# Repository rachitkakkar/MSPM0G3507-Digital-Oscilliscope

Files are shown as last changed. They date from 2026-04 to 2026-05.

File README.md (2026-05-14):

# MSPM0G3507 Digital Storage Oscilloscope

This repository contains the firmware for an Digital Storage Oscilloscope, developed for the Texas Instruments **MSPM0G3507** microcontroller. The project leverages interrupt-driven sampling, real-time graphics rendering to an ST7735 TFT LCD display, and interactive peripherals on a custom PCB designed in KiCAD.

Demo 1
*Low quality GIF displaying oscilloscope at different frequencies*

Demo 1
*Low quality GIF displaying scope at different zoom levels (controlled via slide pot)*

## Features

- **High-Speed Signal Acquisition**: There is a 50 kHz hardware timer interrupt (TimerG6) to sample the ADC and store the value in a storage buffer. The process of sampling and storing into the buffer only occurs on the rising edge of the signal after it passes a trigger set at the half-way mark in order to capture stable waveforms.
- **Real-Time Display**: Live waveform plotting on an ST7735 TFT LCD with grid generation and zoom. Displaying the waveform only occurs when the buffer is full, upon which the 50 kHz TimerG6 interrupt is disabled in order to plot values onto the LCD. Without this crucial step, the microcontroller would be interrupted before it had time to write to the display as that is a comparatively slow task relative to the frequent timer interrupts. In order to further speed up the display (and prevent the flickering of a whole screen redraw), a buffer of previous samples is stored and only the pixels of the previous waveform are cleared. This also requires dynamically fixing the grid in those spots.
- **Interactive Measurements**: 
  - Dual horizontal and vertical cursors to measure $\Delta V$, $\Delta T$.
  - Real-time on-screen calculations for Peak-to-Peak Voltage ($V_{pp}$) and Frequency.
- **Dynamic Controls**:
  - Discrete zoom levels (1x, 2x, 4x) controlled by an ADC-sampled slide potentiometer and downsampling of the ADC sample buffer.
  - Hardware switch integration for playback control (Play/Pause), cursor selection, and precise cursor movement.
  - Input control is handled by another periodic hardware timer interrupt (TimerG12), this time at a frequency of only 30 Hz.
- **Audio Feedback**: DAC-driven sound generation mapped to UI interactions for tactile and auditory feedback. The audio files are downsampled and stored into a C array, where a periodic SysTick interrupt then outputs the values to the 5-bit DAC on the PCB at a frequency of 11 kHz. To prevent noticeable audio distortion, this interrupt is the highest priority.
- **Localization**: Built-in dual-language support (English and Spanish) for the on-screen display.
- **Debugging**: LED based triple toggle to determine latency of interrupt handler.

## Architecture and Key Components

- **`Lab9HMain.cpp`**: The primary entry point. Registers the 30 Hz UI/Game engine timer interrupt, the 50 kHz ADC sampling timer interrupt, the 11 kHz SysTick interrupt, and the main application loop. Also stores code for the corresponding IRQ handlers.
- **`Oscilloscope.cpp` / `.h`**: Core oscilloscope logic. Handles ADC configuration, sample buffering, trigger-level synchronization, and signal metrics calculations (Frequency, $V_{pp}$).
- **`ST7735.cpp` / `.h`**: Display driver for the SPI-based LCD, including routines for drawing bitmaps, characters, and primitive shapes.
- **`Cursor` & `Application`**: Encapsulates the UI state, grid drawing, and cursor boundary/overlap logic.
- **Peripherals**: Interfaces for `Clock`, `Timer`, `Switch`, `SlidePot`, `LED`, `Sound`, and `DAC5`.

## Hardware

- **Microcontroller**: TI MSPM0G3507 LaunchPad
- **Display**: ST7735 SPI LCD (Adafruit REDTAB or HiLetGo BLACKTAB)
- **Inputs**: 
  - Slide Potentiometer (ADC input)
  - 4 Tactile Switches (Digital GPIO)
- **Outputs**: 
  - 5-bit weighted DAC, amplifier chip, and speaker (for audio)
  - LEDs (triple toggle and pause indicator)

The full PCB files are available in the `PCB/` folder
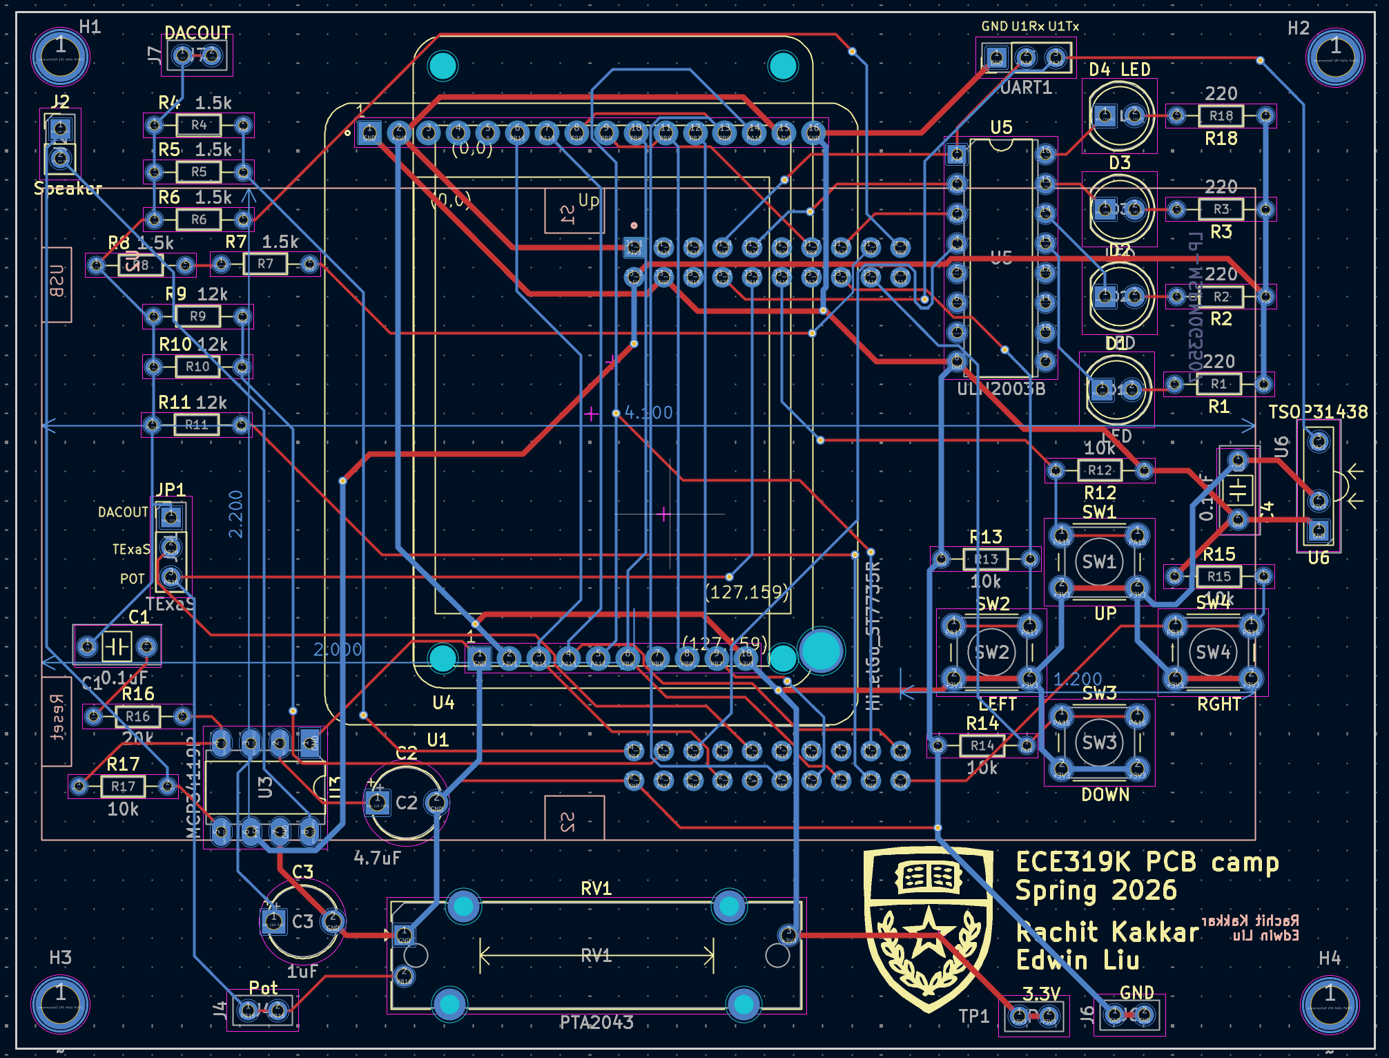
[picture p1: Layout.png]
Layout

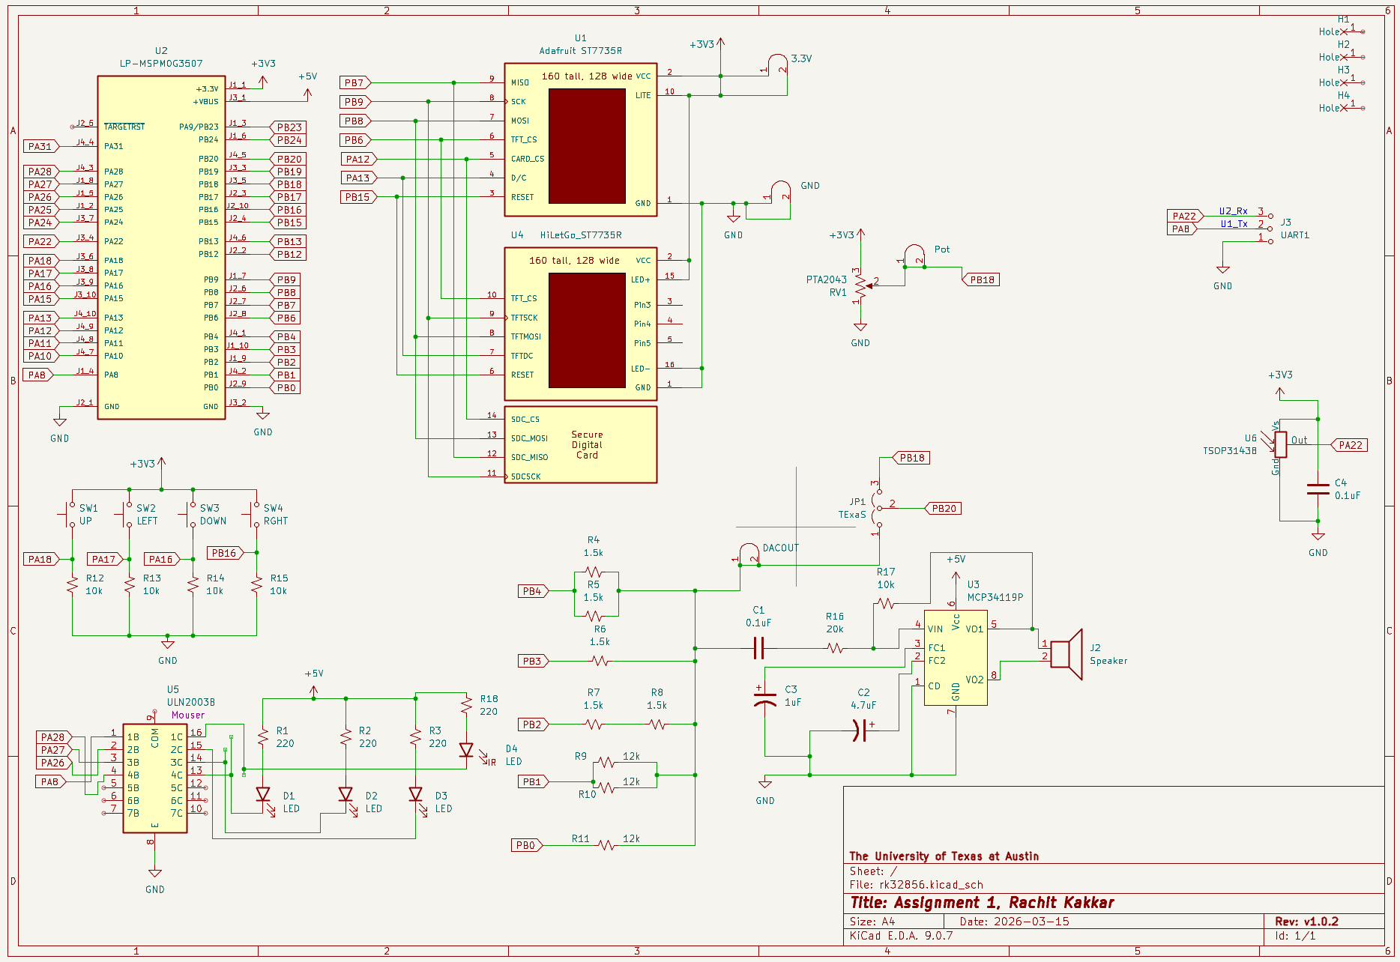
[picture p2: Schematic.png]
Schematic


## Build Instructions

This project is built using Code Composer Studio (CCS) and the TI MSPM0-SDK. 

1. Import the project folder into a Code Composer Studio workspace.
2. Ensure the `MSPM0-SDK` (v2.9.0.01 or compatible) and SysConfig are correctly linked in your project properties.
3. Build the project using the **TI Arm Clang Compiler** (`TICLANG`).
4. Flash the `.out` executable onto the MSPM0G3507 LaunchPad.

## Credits

Much of the starter code for this project was developed by the instructors for ECE319H Course at the University of Texas at Austin.

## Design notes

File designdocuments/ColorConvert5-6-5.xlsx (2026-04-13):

red | green | blue | 565
0 | 255 | 120 | 0x7FE0 | 0x7FE0, // 0, 255, 120

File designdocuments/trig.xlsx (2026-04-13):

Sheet: 64
 | 2 |  | 64
angle | vx | vy | ix | iy
0 | 2 | 0 | 128 | 0
0.09817477042 | 1.990369453 | 0.1960342807 | 127 | 13
0.1963495408 | 1.961570561 | 0.390180644 | 126 | 25
0.2945243113 | 1.913880671 | 0.5805693545 | 122 | 37
0.3926990817 | 1.847759065 | 0.7653668647 | 118 | 49
0.4908738521 | 1.763842529 | 0.9427934737 | 113 | 60
0.5890486225 | 1.662939225 | 1.111140466 | 106 | 71
0.687223393 | 1.546020907 | 1.268786568 | 99 | 81
0.7853981634 | 1.414213562 | 1.414213562 | 91 | 91
0.8835729338 | 1.268786568 | 1.546020907 | 81 | 99
0.9817477042 | 1.111140466 | 1.662939225 | 71 | 106
1.079922475 | 0.9427934737 | 1.763842529 | 60 | 113
1.178097245 | 0.7653668647 | 1.847759065 | 49 | 118
1.276272016 | 0.5805693545 | 1.913880671 | 37 | 122
1.374446786 | 0.390180644 | 1.961570561 | 25 | 126
1.472621556 | 0.1960342807 | 1.990369453 | 13 | 127
1.570796327 | -7.656635742e-16 | 2 | 0 | 128
1.668971097 | -0.1960342807 | 1.990369453 | -13 | 127
1.767145868 | -0.390180644 | 1.961570561 | -25 | 126
1.865320638 | -0.5805693545 | 1.913880671 | -37 | 122
1.963495408 | -0.7653668647 | 1.847759065 | -49 | 118
2.061670179 | -0.9427934737 | 1.763842529 | -60 | 113
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

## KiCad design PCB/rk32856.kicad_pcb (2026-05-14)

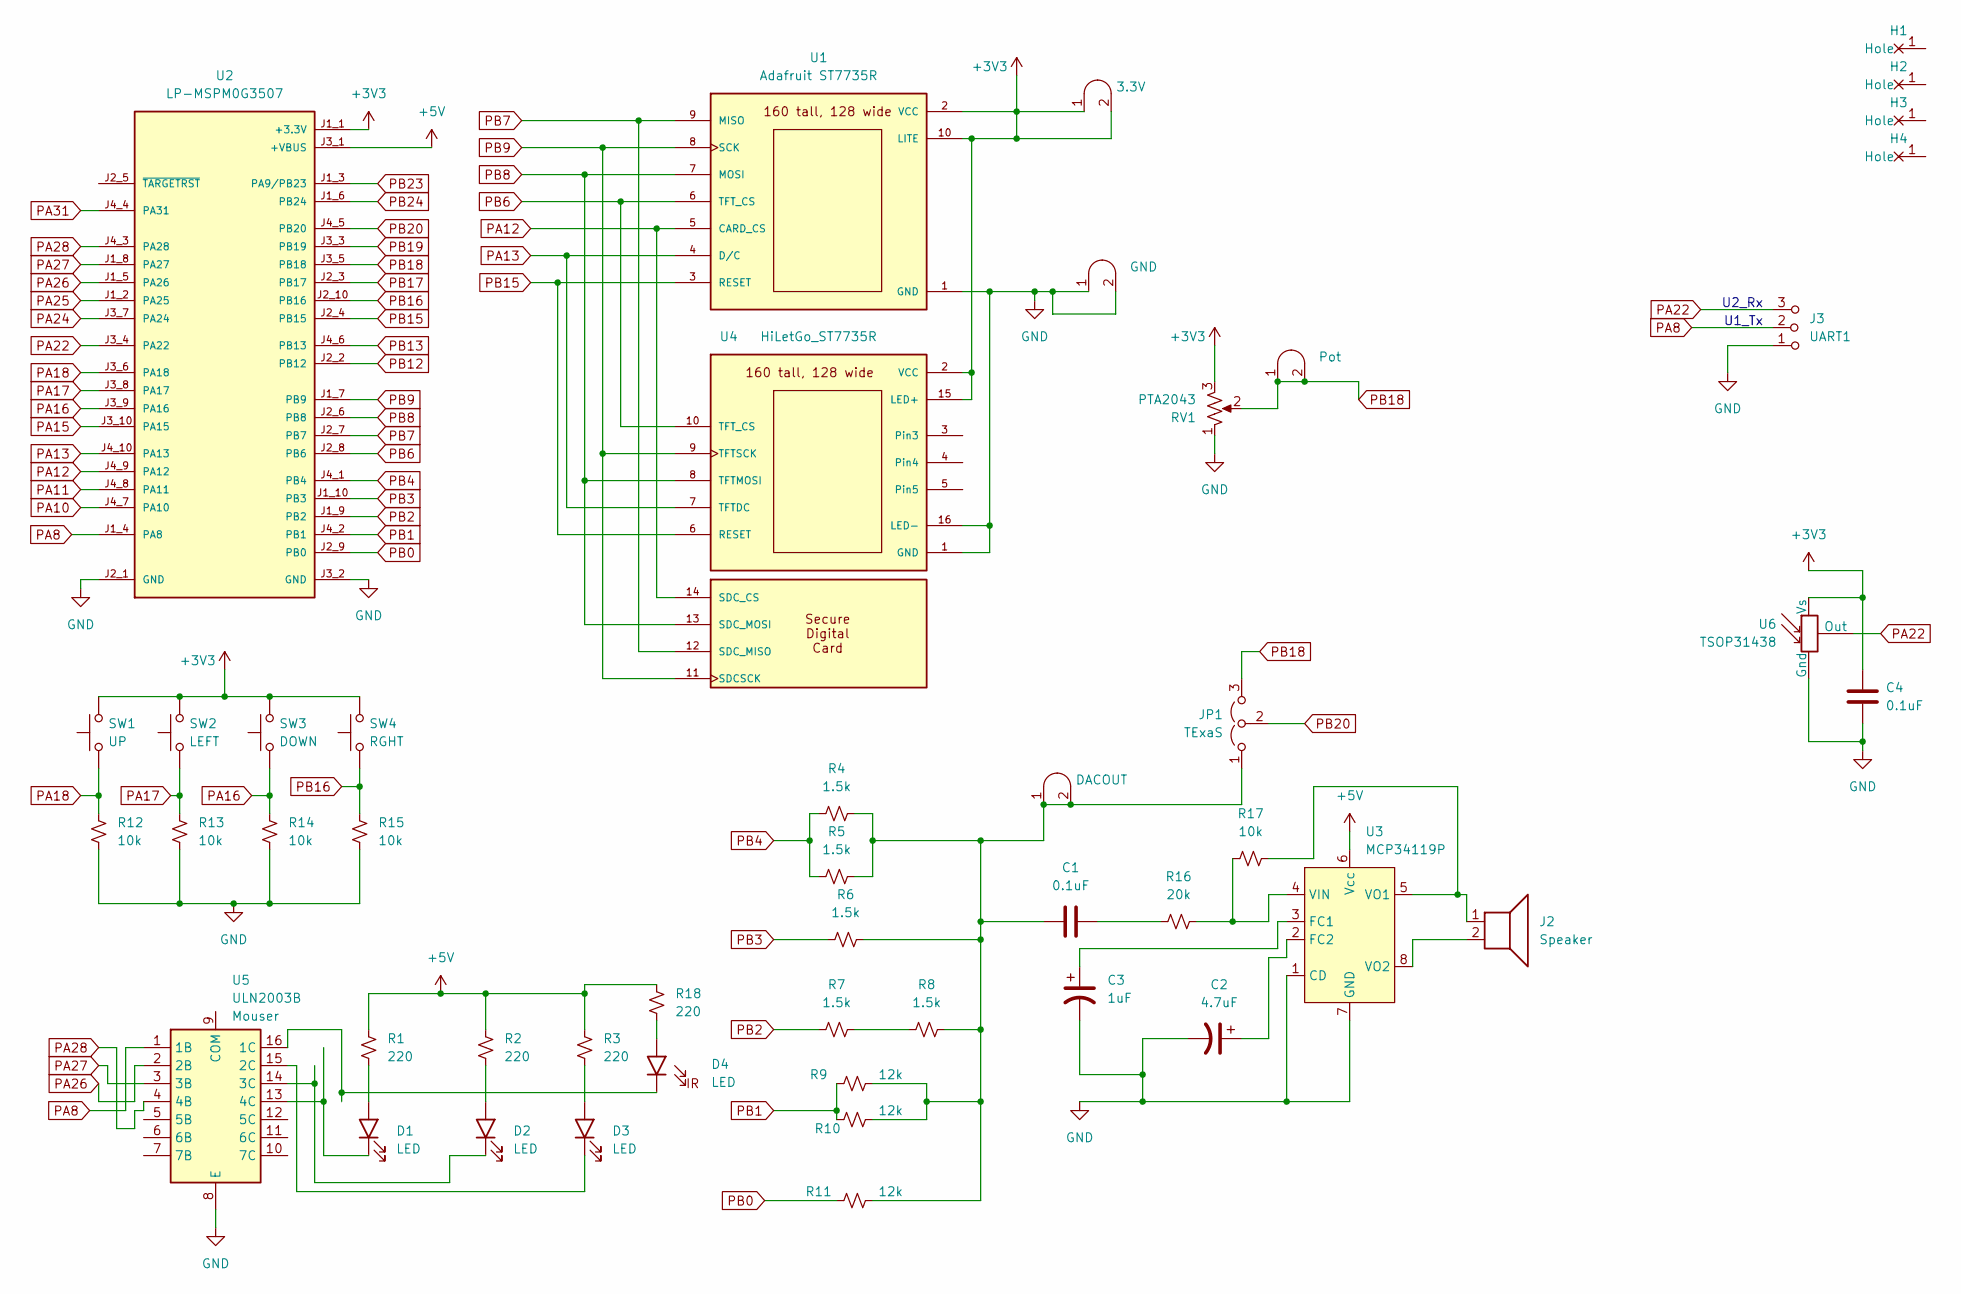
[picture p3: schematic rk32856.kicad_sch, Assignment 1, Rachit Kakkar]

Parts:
C1, C4: 0.1uF; C_Axial_200mil
C2: 4.7uF; CP_Radial_Tantal200mil
C3: 1uF; CP_Radial_Tantal200mil
D1, D2, D3, D4: LED; LED_D5.0mm
H1, H2, H3, H4: MountingHole_4_40
J2: Speaker; PinHeader_1x02_P2.54mm_Vertical
J3: UART1; PinHeader_1x03_P2.54mm_Vertical
J4: Pot; Testpoint_1x02_P2.54mm
J6: GND; Testpoint_1x02_P2.54mm
J7: DACOUT; Testpoint_1x02_P2.54mm
JP1: TExaS; PinHeader_1x03_P2.54mm_Vertical
R1, R2, R3, R18: 220; R_Axial_DIN0204_L3.6mm_D1.6mm_P7.62mm_Horizontal
R4, R5, R6, R7, R8: 1.5k; R_Axial_DIN0204_L3.6mm_D1.6mm_P7.62mm_Horizontal
R9, R10, R11: 12k; R_Axial_DIN0204_L3.6mm_D1.6mm_P7.62mm_Horizontal
R12, R13, R14, R15, R17: 10k; R_Axial_DIN0204_L3.6mm_D1.6mm_P7.62mm_Horizontal
R16: 20k; R_Axial_DIN0204_L3.6mm_D1.6mm_P7.62mm_Horizontal
RV1: PTA2043; PTA2043pot
SW1: UP; SW_PUSH_6mm
SW2: LEFT; SW_PUSH_6mm
SW3: DOWN; SW_PUSH_6mm
SW4: RGHT; SW_PUSH_6mm
TP1: 3.3V; Testpoint_1x02_P2.54mm
U1: Adafruit ST7735R; adafruit_st7735r
U2: LP-MSPM0G3507; ti_LP_MSPM0G3507
U3: MCP34119P; DIP-8_W7.62mm_LongPads
U4: HiLetGo_ST7735R; hiletgo_st7735r
U5: ULN2003B; DIP-16_W7.62mm
U6: TSOP31438

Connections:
+3V3: C4.1, RV1.3, SW1.2, SW2.2, SW3.2, SW4.2, TP1.1 (A), TP1.2 (B), U1.2 (VCC), U1.10 (LITE), U2.J1_1 (+3.3V), U4.2 (VCC), U4.15 (LED+), U6.2 (Vs)
+5V: R1.1, R2.1, R3.1, R18.1, U2.J3_1 (+VBUS), U3.6 (Vcc)
GND: C2.2, C3.2, C4.2, J3.1 (A), J6.1 (A), J6.2 (B), R12.2, R13.2, R14.2, R15.2, RV1.1, U1.1 (GND), U2.J2_1 (GND), U2.J3_2 (GND), U3.1 (CD), U3.7 (GND), U4.1 (GND), U4.16 (LED-), U5.8 (E), U6.1 (Gnd)
unnamed: C1.2, R16.1
unnamed: D1.2 (A), R1.2
unnamed: D1.1 (K), U5.13 (4C)
unnamed: D2.2 (A), R2.2
unnamed: D2.1 (K), U5.14 (3C)
unnamed: D3.2 (A), R3.2
unnamed: D3.1 (K), U5.15 (2C)
unnamed 10: D4.2 (A), R18.2; also elsewhere on the board
unnamed 11: D4.1 (K), U5.16 (1C); also elsewhere on the board
unnamed: C1.1, J7.1 (A), J7.2 (B), JP1.1 (A), R4.1, R5.1, R6.1, R8.1, R9.1, R10.1, R11.1
unnamed: R7.1, R8.2
unnamed: C3.1, U3.3 (FC1)
unnamed: C2.1, U3.2 (FC2)
unnamed: R16.2, R17.1, U3.4 (VIN)
unnamed: J2.1, R17.2, U3.5 (VO1)
unnamed: J2.2, U3.8 (VO2)
PA8: J3.2 (B), U2.J1_4 (PA8), U5.1 (1B)
PA10: U2.J4_7 (PA10)
PA11: U2.J4_8 (PA11)
PA12: U1.5 (CARD_CS), U2.J4_9 (PA12), U4.14 (SDC_CS)
PA13: U1.4 (D/C), U2.J4_10 (PA13), U4.7 (TFTDC)
PA15: U2.J3_10 (PA15)
PA16: R14.1, SW3.1, U2.J3_9 (PA16)
PA17: R13.1, SW2.1, U2.J3_8 (PA17)
PA18: R12.1, SW1.1, U2.J3_6 (PA18)
PA22: J3.3 (C), U2.J3_4 (PA22), U6.3 (Out)
PA24: U2.J3_7 (PA24)
PA25: U2.J1_2 (PA25)
PA26: U2.J1_5 (PA26), U5.2 (2B)
PA27: U2.J1_8 (PA27), U5.3 (3B)
PA28: U2.J4_3 (PA28), U5.4 (4B)
PA31: U2.J4_4 (PA31)
PB0: R11.2, U2.J2_9 (PB0)
PB1: R9.2, R10.2, U2.J4_2 (PB1)
PB2: R7.2, U2.J1_9 (PB2)
PB3: R6.2, U2.J1_10 (PB3)
PB4: R4.2, R5.2, U2.J4_1 (PB4)
PB6: U1.6 (TFT_CS), U2.J2_8 (PB6), U4.10 (TFT_CS)
PB7: U1.9 (MISO), U2.J2_7 (PB7), U4.12 (SDC_MISO)
PB8: U1.7 (MOSI), U2.J2_6 (PB8), U4.8 (TFTMOSI), U4.13 (SDC_MOSI)
PB9: U1.8 (SCK), U2.J1_7 (PB9), U4.9 (TFTSCK), U4.11 (SDCSCK)
PB12: U2.J2_2 (PB12)
PB13: U2.J4_6 (PB13)
PB15: U1.3 (RESET), U2.J2_4 (PB15), U4.6 (RESET)
PB16: R15.1, SW4.1, U2.J2_10 (PB16)
PB17: U2.J2_3 (PB17)
PB18: J4.1 (A), J4.2 (B), JP1.3 (B), RV1.2, U2.J3_5 (PB18)
PB19: U2.J3_3 (PB19)
PB20: JP1.2 (C), U2.J4_5 (PB20)
PB23: U2.J1_3 (PA9/PB23)
PB24: U2.J1_6 (PB24)

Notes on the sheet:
U2_Rx
U1_Tx

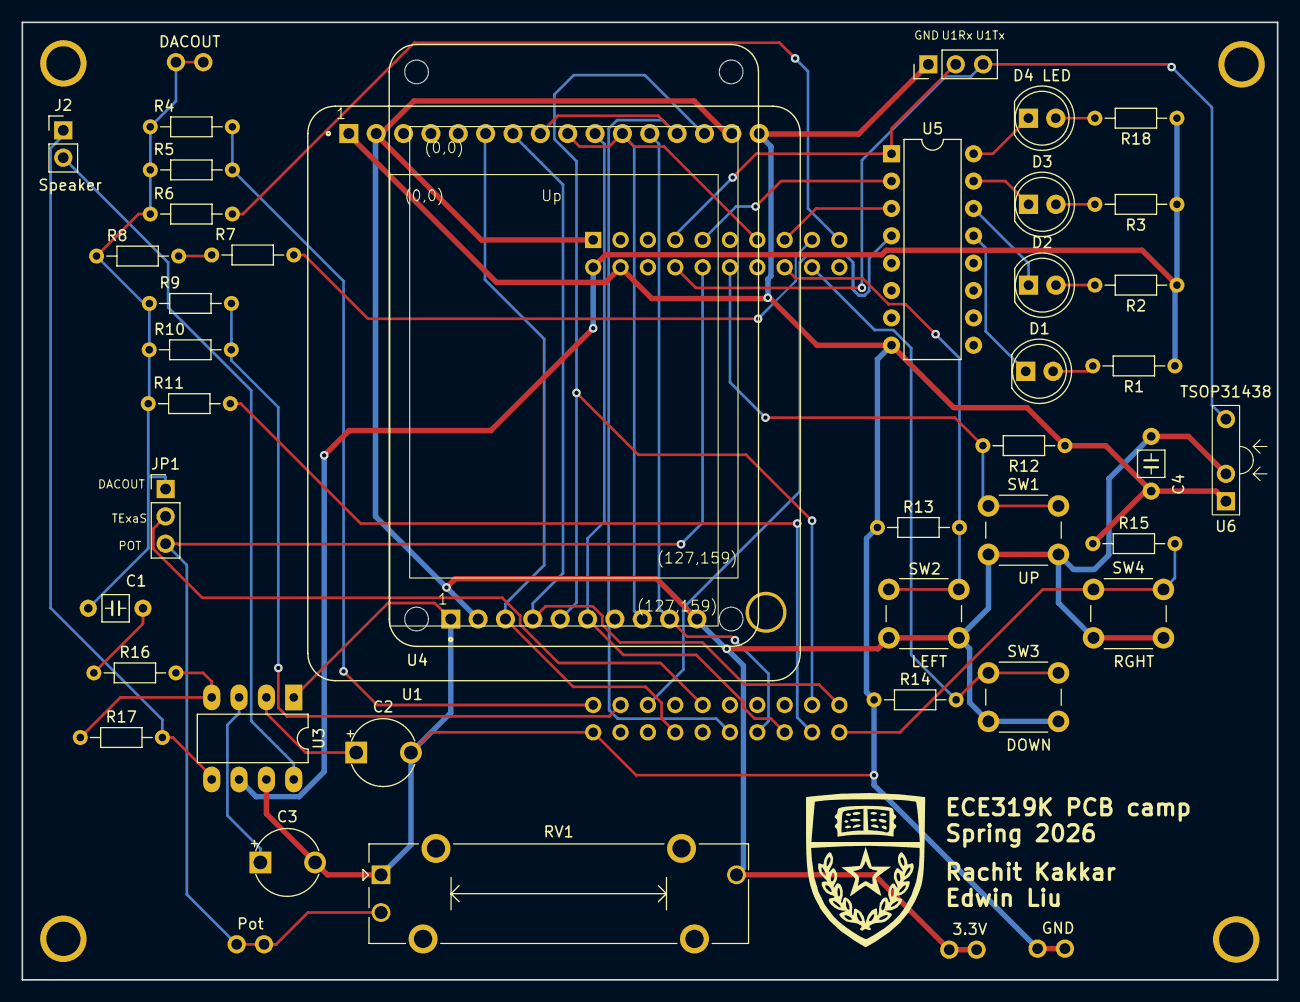
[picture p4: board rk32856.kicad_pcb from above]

Board: 2 copper layers, 116.5 x 88.9 mm, 48 parts (1 on the bottom side), 42 nets.

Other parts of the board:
D4 LED: LED; LED_D5.0mm

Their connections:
unnamed 10: D4 LED.2 (A); also elsewhere on the board
unnamed 11: D4 LED.1 (K); also elsewhere on the board

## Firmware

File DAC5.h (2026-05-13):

/**
 * @file      DAC5.h
 * @brief     5-bit binary-weighted DAC
 * @details   Lab 5. Digital Piano using a Digital to Analog Converter<br>
 * For more information see<br> https://docs.google.com/document/d/1DVmHjqsx24FvLp4x8KKyr5UmDeDlBlfeQPsVvKFQF_k/edit<br>
 * @version   ECE319K Fall 2025
 * @author    Your names go here
 * @copyright Lab solution, do not post,
 * @warning   AS-IS
 * @note      For more information see  http://users.ece.utexas.edu/~valvano/
 * @date      July 19, 2025
  <table>
<caption id="Lab5pins">Pins on the 5-bit DAC</caption>
<tr><th>Pin <th>GPIO<th>Hardware
<tr><td>PB4 <td>output<td>bit 4 (most significant)
<tr><td>PB3 <td>output<td>bit 3
<tr><td>PB2 <td>output<td>bit 2
<tr><td>PB1 <td>output<td>bit 1
<tr><td>PB0 <td>output<td>bit 0 (least significant)
</table>
  ******************************************************************************/
#ifndef __DAC5_H__
#define __DAC5_H__

/**
 * Initialize 5-bit DAC
 *    - PB4 output MSBit
 *    - PB3 output
 *    - PB2 output
 *    - PB1 output
 *    - PB0 output LSBit
 * @param none
 * @return none
 * @brief  Initialize DAC
 * @note LaunchPad_Init has been called; this program should not reset Port B
 */
void DAC5_Init(void);

/**
 * Output to 5-bit DAC
 * @param data is 5-bit value to output, 0 to 31
 * @return none
 * @brief  Output to DAC5
 * @note this solution must be friendly
 */
void DAC5_Out(uint32_t data);

#endif // __DAC5_H__

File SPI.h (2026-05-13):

/*!
 * @defgroup SPI
 * @brief Synchronous serial communication
 <table>
<caption id="SPIpins">SPI-LCD pins </caption>
<tr><th>Pin <th>Function  <th>Description
<tr><td>PB9 <td>SPI1 SCLK <td>J1.7 LCD SPI clock (SPI)   
<tr><td>PB6 <td>SPI1 CS0  <td>J2.13 LCD SPI CS (SPI)     
<tr><td>PB8 <td>SPI1 PICO <td>J2.15 LCD SPI data (SPI)    
<tr><td>PB15<td>GPIO      <td>J2.17 LCD !RST =1 for run, =0 for reset   
<tr><td>PA13<td>GPIO      <td>J4.31 LCD RS =1 for data, =0 for command   
</table>
 * @{*/
/**
 * @file      SPI.h
 * @brief     Synchronous serial communication
 * @details   SPI uses a chip select, clock, data out and data in. This interface does not use data in.
 * This interface can be used for MKII LCD and the ST7735R LCD
 * \image html SPIinterface.png  width=500px
 * @version   ECE319K v1.2
 * @author    Daniel Valvano and Jonathan Valvano
 * @copyright Copyright 2025 by Jonathan W. Valvano, valvano@mail.utexas.edu,
 * @warning   AS-IS
 * @note      For more information see  http://users.ece.utexas.edu/~valvano/
 * @date      July 19, 2025
 <table>
<caption id="SPIpins2">SPI-LCD pins </caption>
<tr><th>Pin <th>Function  <th>Description
<tr><td>PB9 <td>SPI1 SCLK <td>J1.7 LCD SPI clock (SPI)   
<tr><td>PB6 <td>SPI1 CS0  <td>J2.13 LCD SPI CS (SPI)     
<tr><td>PB8 <td>SPI1 PICO <td>J2.15 LCD SPI data (SPI)    
<tr><td>PB15<td>GPIO      <td>J2.17 LCD !RST =1 for run, =0 for reset  
<tr><td>PA13<td>GPIO      <td>J4.31 LCD RS =1 for data, =0 for command   
</table>
  ******************************************************************************/
#ifndef __SPI_H__
#define __SPI_H__


/**
 * Initialize SPI for 8 MHz baud clock
 * using busy-wait synchronization.
 * Calls Clock_Freq to get bus clock
 * - PB9 SPI1 SCLK   
 * - PB6 SPI1 CS0       
 * - PB8 SPI1 PICO  
 * - PB15 GPIO !RST =1 for run, =0 for reset    
 * - PA13 GPIO RS =1 for data, =0 for command
 *
 * @note SPI0,SPI1 in power domain PD1 SysClk equals bus CPU clock
 * @param none
 * @return none 
 * @brief initialize SPI
 */
void SPI_Init(void);

/**
 * Output 8-bit data to SPI port.
 * RS=PA13=1 for data.
 * @param data is an 8-bit data to be transferred
 * @return none 
 * @brief Output data
 */
void SPI_OutData(char data);

/**
 * Output 8-bit command to SPI port.
 * RS=PA13=0 for command
 * @param  command is an 8-bit command to be transferred
 * @return none 
 * @brief Output command
 */
void SPI_OutCommand(char command);

/**
 *  Reset LCD 
 * -# drive RST high for 500ms
 * -# drive RST low for 500ms
 * -# drive RST high for 500ms
 * 
 * @param none
 * @return none 
 * @brief Reset LCD
 */
void SPI_Reset(void);
#endif // __SPI_H__
/** @}*/

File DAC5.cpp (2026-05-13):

/* DAC5.cpp
 * Students put your names here
 * Modified: December 26, 2024
 * 5-bit binary-weighted DAC connected to PB4-PB0
 */
#include <ti/devices/msp/msp.h>
#define PB0INDEX  11 // UART0_TX  SPI1_CS2  TIMA1_C0  TIMA0_C2
#define PB1INDEX  12 // UART0_RX  SPI1_CS3  TIMA1_C1  TIMA0_C2N
#define PB2INDEX  14 // UART3_TX  UART2_CTS I2C1_SCL  TIMA0_C3  UART1_CTS TIMG6_C0  TIMA1_C0
#define PB3INDEX  15 // UART3_RX  UART2_RTS I2C1_SDA  TIMA0_C3N UART1_RTS TIMG6_C1  TIMA1_C1
#define PB4INDEX  16 // UART1_TX  UART3_CTS TIMA1_C0  TIMA0_C2  TIMA1_C0N

// **************DAC5_Init*********************
// Initialize 5-bit DAC, called once
// Input: none
// Output: none
void DAC5_Init(void){
// Assumes LaunchPad_Init has been called
// I.e., PortB has already been reset and activated (do not reset PortB here again)
     // write this
  IOMUX->SECCFG.PINCM[PB2INDEX] = 0x81;
  IOMUX->SECCFG.PINCM[PB1INDEX] = 0x81;
  IOMUX->SECCFG.PINCM[PB0INDEX] = 0x81;

  IOMUX->SECCFG.PINCM[PB3INDEX] = 0x81;
  IOMUX->SECCFG.PINCM[PB4INDEX] = 0x81;
  
  GPIOB->DOE31_0 |= (1 << 0);
  GPIOB->DOE31_0 |= (1 << 1);
  GPIOB->DOE31_0 |= (1 << 2);
  
  GPIOB->DOE31_0 |= (1 << 3);
  GPIOB->DOE31_0 |= (1 << 4);

}

// **************DAC5_Out*********************
// output to DAC5
// Input: 5-bit data, 0 to 31
// Input=n is converted to n*3.3V/31
// Output: none
// Note: this solution must be friendly
void DAC5_Out(uint32_t data){
     // write this

     GPIOB->DOUTCLR31_0 = (1 << 0);
     GPIOB->DOUTCLR31_0 = (1 << 1);
     GPIOB->DOUTCLR31_0 = (1 << 2);
     GPIOB->DOUTCLR31_0 = (1 << 3);
     GPIOB->DOUTCLR31_0 = (1 << 4);
     GPIOB->DOUTSET31_0 = data;
}

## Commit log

2026-04-13 Add inital sampling of ADC (10kHz timer interrupt) and plotting to LCD grid
    [ColorConvert5-6-5.xlsx, trig.xlsx]
2026-04-17 Get oscilliscope to fully work for signals up to 100 Hz, start horizontal measurement cursors
2026-05-14 Add an extensive README and perform minor code clean-up
    [rk32856.kicad_pcb, rk32856.kicad_sch]
